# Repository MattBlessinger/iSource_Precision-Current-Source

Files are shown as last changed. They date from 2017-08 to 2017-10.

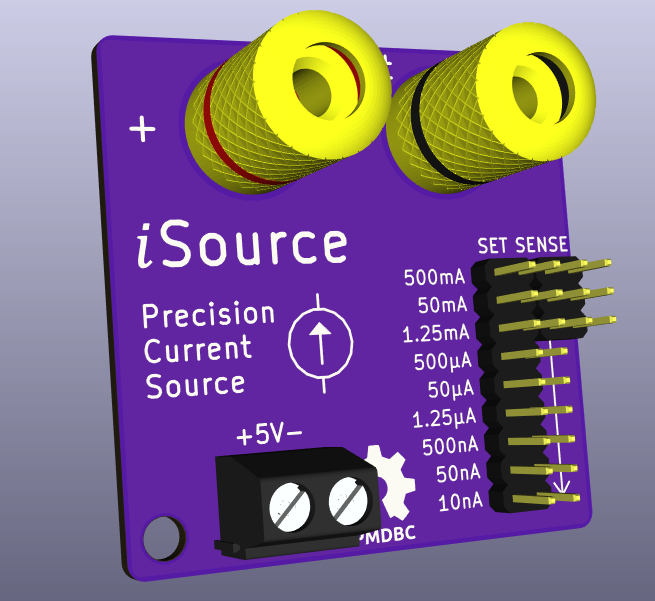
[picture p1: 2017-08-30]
3D top iso.png

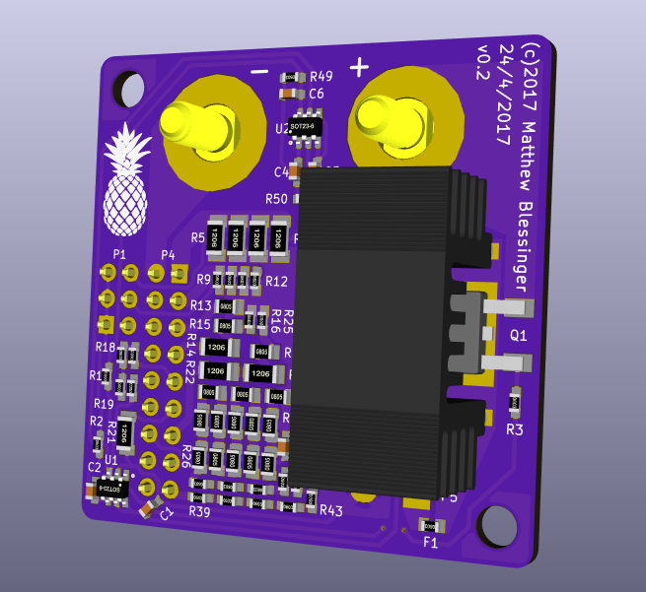
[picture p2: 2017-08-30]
3D bottom iso.png

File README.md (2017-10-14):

# Precision-Current-Source
Low-cost precision current source for calibrating multimeters, ammeters, current shunts, etc.

### Overview
The current source is based on an electronic load in which an op amp sets a known voltage drop across precision resistors. To maintain accuracy, the set-point voltage is constant and sourced by the MAX6070 low-noise, high-precision voltage reference. Different currents are selected by changing the shunt resistors with a pin header jumper. The initial accuracy without tuning (determined by detailed calculations) is <0.1% for 500mA, <0.1% for currents of 50mA to 500nA, <0.2% for 50nA, and <0.5% for 10nA. The measured accuracy was found to be within the expected values except for the nA ranges, likely due to measurement error (see the results spreadsheet file).

### Usage
To use the current source, connect the device under test (DUT) (multimeter, etc.) to the Output +/- 4mm banana connectors on the iSource. (This setup is high-side current sensing.) Put the current set and sense jumpers in the desired position; note that the bottom sense position applies to the set currents of 1.25mA and below. Connect power leads to the screw terminal block and apply power. The current set and sense jumpers can be changed while power is applied without harming the iSource.

### Design
The electronic load design is well-known amongst the electronics community. A commonly referenced design is "EEVBlog 102 – DIY Constant Current Dummy Load for Power Supply and Battery Test." In short, the op amp controls the mosfet's gate voltage to vary the voltage drop across shunt resistors between the mosfet source and ground. The voltage drop is fed to the inverting input of the op amp to provide closed-loop feedback. The set point voltage is routed to the non-inverting input of the op amp. The difference from an electronic load is that the set point voltage does not vary, instead it is constant and supplied by a precision voltage reference. To change the current, the shunt resistors are changed. The DUT is wired between Vdd and the mosfet drain.

The current ranges were chosen based on my initial desire to calibrate my 6000 count multimeter and the EEVBlog uCurrent, hence the 50, 500 and 1250 values. The ranges can be changed by using different resistor combinations. The banana jacks are spaced at the industry standard 0.75". The power input is labeled as 5V but can work down to 4V, e.g. Li-Ion cell. Pin headers and jumpers were used to select the current ranges since low-leakage JFETs can't handle the higher current ranges, and dip switches can't switch the higher either. A parallel load was added to impose a minimum 3mA current through the mosfet to eliminate leakage current issues in the nA ranges. Separate sense pins are used for the 50 and 500mA ranges to account for voltage drop along the tracks due to the higher current. (Voltage drop along the tracks are included in the accuracy calculations for all current ranges.) A DPAK mosfet was used in order to use a heatsink since the mosfet will dissipate a fair amount of heat at 500mA range. It is desired to take the heat away from the PCB in order to not heat the resistors, op amp and voltage reference.

The component choices typically came down to accuracy and cost. The voltage reference gives 0.04% initial accuracy and low thermal drift for $3.35 in one off quantities. The op amp has low input offset voltage (8uV), low input offset current (5pA), and low gain-bandwidth product (80kHz) to prevent the common ringing problem, all for $1.15 in one off quantities. The highest precision resistors were used for a each current range, so cost was minimized by the selection of resistor combinations.

### Accuracy
Several steps were taken to account for the current-induced voltage drop along tracks. As previously mentioned separate sense pins are used for 50 and 500mA so that separate tracks are run to the net-zero middle of the resistor pack. The op amp's ground is run to the net-zero middle of 500mA resistor ground pack since it has the greatest voltage drop. A large ground pour is used to minimuze the resistance between the ground of the op amp and rest of the current ranges' ground return.

Extensive calculations were performed to determine the maximum guaranteed tolerance for an as-built unit. (I did not want to rely on tuning each current range.) The calculations assume worst case scenario for all specifications provided in data sheets, thus the numbers ought to be maximum accuracy values. The parameters included in the accuracy calculations are:
* **Voltage reference**: initial accuracy, thermal drift, thermal hysteresis
* **Resistors**: tolerance, thermal coefficient
* **Op amp**: offset voltage, input bias current, input offset current
* **Track resistance**: resistance from sense pin to first resistor, resistance from last resistor to voltage reference ground, optimized track routing of high-current settings

### Results
I measured the accuracy with a Keysight 34465A 6.5 digit DMM with a 4 month old calibration. The 34465A has a low current range of 1uA with 1pA resolution. I used a single cell lithium ion battery charged to 4.2V to power the iSource. I placed the battery and iSource in a cast aluminum case to minimize EMI. The output was wired to the 34465A with an unshielded twisted pair wires. I used remote logging via PyVISA to remove myself from the measurement area. The 34465A was warmed up for 1 hour, and each current range was allowed to settle for 5 minutes before collecting data, although the currents settled within 10-30 seconds. I took 500 measurements with 10 NPLC at the lowest 34465A current range possible.

The spreadsheet shows the average value, accuracy % based on the measured average, 34465A uncertainty, and standard deviation of the 500 measurements. I suspect the increased inaccuracy of nA ranges is due to my measurement setup as I do not know all the proper techniques nor have the proper setup for them.

### Cost
As of June, 2017, the total build cost was $48 including the OSHPark PCB not listed in the BOM. Lower tolerance resistors may be used to significantly reduce the cost. New accuracy calculations can be performed by changing the resistor tolerance in the spreadsheet.

### License
The project is licensed as open source hardware and Creative Commons Attribution-ShareAlike 3.0 (CC BY-SA 3.0 US)

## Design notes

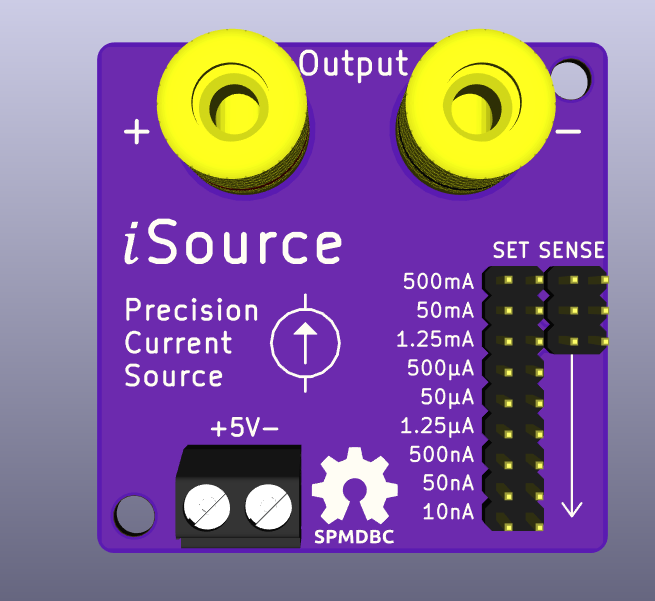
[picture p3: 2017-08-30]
3D top.png

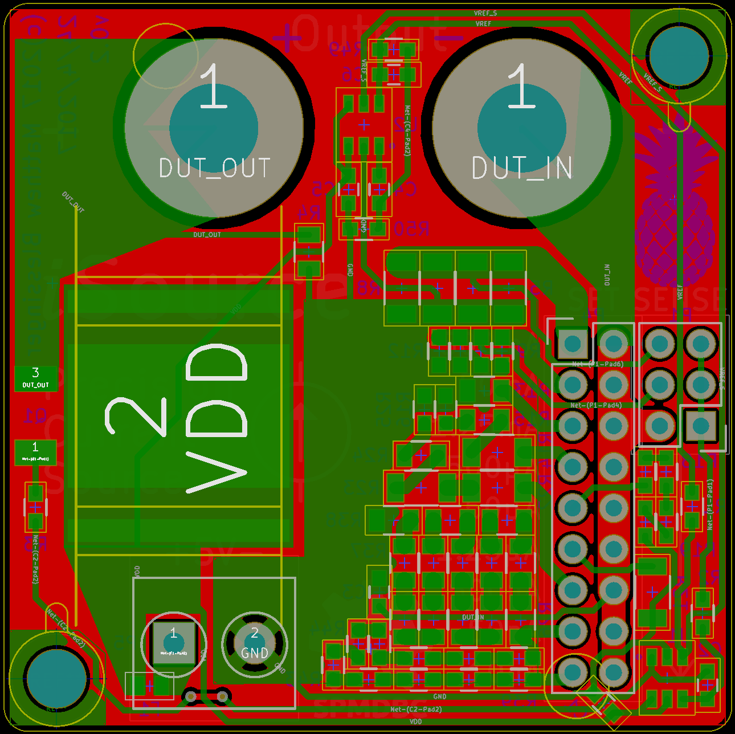
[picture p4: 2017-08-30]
PCB bottom layer.png

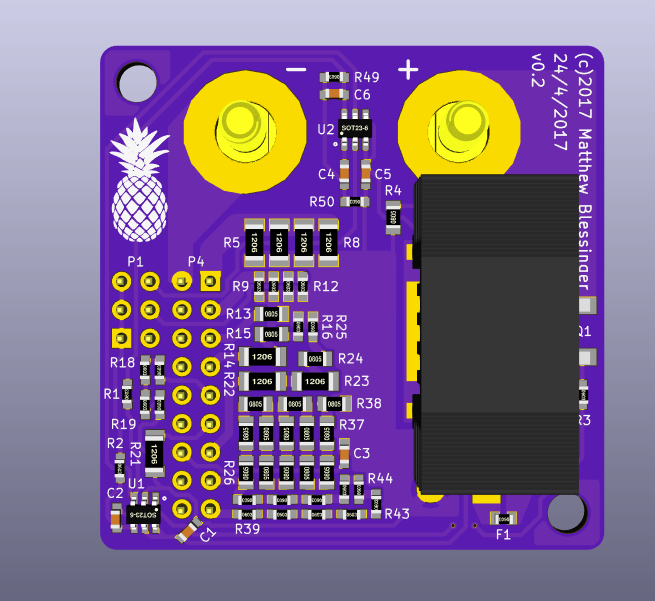
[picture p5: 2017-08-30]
3D bottom.png

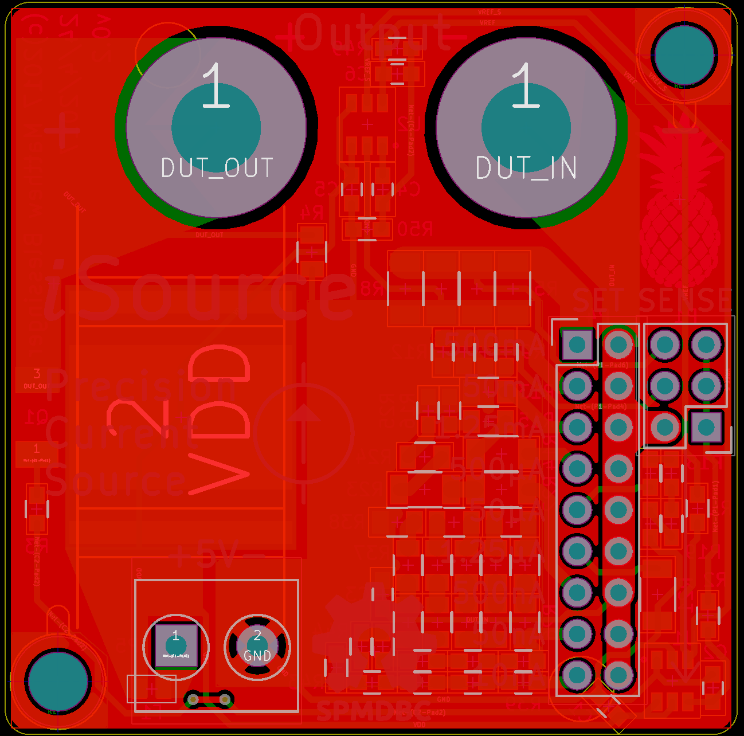
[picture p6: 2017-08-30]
PCB top layer.png

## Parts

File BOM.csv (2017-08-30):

Reference | Value | Footprint | Datasheet | Product ID | Manufacturer | Tolerance
C1 | 0.1uF | MKB:C_0603 |  | GCM188R71H104KA57D | Murata
C5 | 0.1uF | MKB:C_0603 |  | GCM188R71H104KA57D | Murata
C6 | 0.1uF | MKB:C_0603 |  | GCM188R71H104KA57D | Murata
C4 | 0.1uF | MKB:C_0603 |  | GCM188R71H104KA57D | Murata
R50 | 0R | MKB:R_0603 |  | RC0603FR-072KL | Yageo | 1%
R9 | 100R | MKB:R_0603 |  | APC0603T100RZ | Ohmite | 0.01%
R10 | 100R | MKB:R_0603 |  | APC0603T100RZ | Ohmite | 0.01%
R11 | 100R | MKB:R_0603 |  | APC0603T100RZ | Ohmite | 0.01%
R12 | 100R | MKB:R_0603 |  | APC0603T100RZ | Ohmite | 0.01%
R3 | 100R | MKB:R_0603 |  | RC0603FR-07100RL | Yageo
R17 | 10k | MKB:R_0603 |  | APC0603T10K0Z | Ohmite | 0.01%
R18 | 10k | MKB:R_0603 |  | APC0603T10K0Z | Ohmite | 0.01%
R2 | 10k | MKB:R_0603 |  | RC0603FR-0710KL | Yageo
R39 | 10M | MKB:R_0603 |  | CRCW060310M0DHEAP | Vishay Dale | 0.50%
R40 | 10M | MKB:R_0603 |  | CRCW060310M0DHEAP | Vishay Dale | 0.50%
R41 | 10M | MKB:R_0603 |  | CRCW060310M0DHEAP | Vishay Dale | 0.50%
R42 | 10M | MKB:R_0603 |  | CRCW060310M0DHEAP | Vishay Dale | 0.50%
R43 | 10M | MKB:R_0603 |  | CRCW060310M0DHEAP | Vishay Dale | 0.50%
R44 | 10M | MKB:R_0603 |  | CRCW060310M0DHEAP | Vishay Dale | 0.50%
R45 | 10M | MKB:R_0603 |  | CRCW060310M0DHEAP | Vishay Dale | 0.50%
R46 | 10M | MKB:R_0603 |  | CRCW060310M0DHEAP | Vishay Dale | 0.50%
R47 | 10M | MKB:R_0603 |  | CRCW060310M0DHEAP | Vishay Dale | 0.50%
R48 | 10M | MKB:R_0603 |  | CRCW060310M0DHEAP | Vishay Dale | 0.50%
C2 | 10nF | MKB:C_0603 |  | GRM188R71H103JA01D | Murata
R20 | 10R | MKB:R_0603 |  | RC0603FR-0710RL | Yageo | 1%
R5 | 10R | MKB:R_1206 |  | RNCF1206AKT10R0 | Stackpole Electronics | 0.05%
R6 | 10R | MKB:R_1206 |  | RNCF1206AKT10R0 | Stackpole Electronics | 0.05%
R7 | 10R | MKB:R_1206 |  | RNCF1206AKT10R0 | Stackpole Electronics | 0.05%
R8 | 10R | MKB:R_1206 |  | RNCF1206AKT10R0 | Stackpole Electronics | 0.05%
R13 | 1k | MKB:R_0805 |  | APC0805T1K00Z | Ohmite | 0.01%
R38 | 1M | MKB:R_0805 |  | CPF0805B1M0E1 | TE Connectivity | 0.10%
R21 | 1M | MKB:R_1206 |  | RG3216N-1004-W-T1 | Susumu | 0.05%
R22 | 1M | MKB:R_1206 |  | RG3216N-1004-W-T1 | Susumu | 0.05%
R23 | 1M | MKB:R_1206 |  | RG3216N-1004-W-T1 | Susumu | 0.05%
R16 | 1R | MKB:R_0603 |  | RC0603FR-071RL | Yageo | 1%
C3 | 1uF | MKB:C_0603 |  | GCM188R71H104KA57D | Murata
R1 | 270R | MKB:R_0603 |  | RC0603FR-07270RL | Yageo
R14 | 2k | MKB:R_1206 |  | APC1206T2K00Z | Ohmite | 0.01%
R49 | 2k | MKB:R_0603 |  | RC0603FR-072KL | Yageo | 1%
R26 | 2M | MKB:R_0805 |  | CPF0805B2M0E1 | TE Connectivity | 0.10%
R27 | 2M | MKB:R_0805 |  | CPF0805B2M0E1 | TE Connectivity | 0.10%
R28 | 2M | MKB:R_0805 |  | CPF0805B2M0E1 | TE Connectivity | 0.10%
R29 | 2M | MKB:R_0805 |  | CPF0805B2M0E1 | TE Connectivity | 0.10%
R30 | 2M | MKB:R_0805 |  | CPF0805B2M0E1 | TE Connectivity | 0.10%
R31 | 2M | MKB:R_0805 |  | CPF0805B2M0E1 | TE Connectivity | 0.10%
R32 | 2M | MKB:R_0805 |  | CPF0805B2M0E1 | TE Connectivity | 0.10%
R33 | 2M | MKB:R_0805 |  | CPF0805B2M0E1 | TE Connectivity | 0.10%
R34 | 2M | MKB:R_0805 |  | CPF0805B2M0E1 | TE Connectivity | 0.10%
R35 | 2M | MKB:R_0805 |  | CPF0805B2M0E1 | TE Connectivity | 0.10%
R36 | 2M | MKB:R_0805 |  | CPF0805B2M0E1 | TE Connectivity | 0.10%
R37 | 2M | MKB:R_0805 |  | CPF0805B2M0E1 | TE Connectivity | 0.10%
R25 | 30k | MKB:R_0603 |  | RG1608N-303-W-T1 | Susumu | 0.05%
R24 | 470k | MKB:R_0805 |  | RG2012N-474-W-T1 | Susumu | 0.05%
R4 | 470R | MKB:R_0805 |  | RC0805FR-07470RL | Yageo
R15 | 499R | MKB:R_0805 |  | APC0805T499RZ | Ohmite | 0.01%
R19 | 4k99 | MKB:R_0603 |  | APC0603T4K99Z | Ohmite | 0.01%
F1 | 750mA | MKB:FUSE_0603 |  | C2Q 750 | Bel Fuse
P2 | CONN_01X01 | MKB:Binding_post_4mm |  | _ | _
P3 | CONN_01X01 | MKB:Binding_post_4mm |  | _ | _
P5 | CONN_01X02 | MKB:TerminalBlock_Pheonix_MKDS1.5-2pol_1985849 |  | 1985849 | Phoenix Contact
P1 | CONN_02X03 | Pin_Headers:Pin_Header_Straight_2x03
P4 | CONN_02X09 | Pin_Headers:Pin_Header_Straight_2x09
U2 | MAX6070 | MKB:SOT-23-6 |  | MAX6070AAUT12+T | Maxim Integrated
U1 | MCP6V11T-E/OT | MKB:SOT-23-6 |  | MCP6V11T-E/OT | Microchip
Q1 | Q_NMOS_GDS | MKB:TO-252_wHeatsink |  | BUK92150-55A_118 | Nexperia
 | case |  |  | 1551RBK | Hammond Manufacturing
 | heat sink |  |  | 219-263A-TR | Wakefield-Vette

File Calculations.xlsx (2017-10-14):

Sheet: Summary
I_designed [A] | U_designed [%] | I_measured [A] | U_measured [%]
0.5 | 0.1364
0.05 | 0.0791 | 0.04999793058 | 0.0041
0.00125 | 0.0789 | 0.0012498142 | 0.0149
0.0005 | 0.0758 | 0.0004999797453 | 0.0041
5e-05 | 0.0750 | 4.999951055e-05 | 0.0010
1.25e-06 | 0.1146 | 1.250664623e-06 | 0.0532
5e-07 | 0.1146 | 5.0069806e-07 | 0.1396
5e-08 | 0.1647 | 5.063922111e-08 | 1.2784
1e-08 | 0.4866 | 1.064807622e-08 | 6.4808

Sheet: Measurements
I_designed [A] | I_measured [A] | Error [%] | Standard dev [A] | Uncertainty [A] | Uncertainty [%]
0.5
0.05 | 0.04999793058 | -0.0041 | 1.492796574e-07 | 2.999896529e-05 | 0.0600
0.00125 | 0.0012498142 | -0.0149 | 3.650786754e-08 | 2.6249071e-06 | 0.2100
0.0005 | 0.0004999797453 | -0.0041 | 1.001276153e-09 | 2.999898727e-07 | 0.0600
5e-05 | 4.999951055e-05 | -0.0010 | 1.323088922e-10 | 2.599975528e-08 | 0.0520
1.25e-06 | 1.250664623e-06 | 0.0532 | 9.79271387e-11 | 8.253323114e-10 | 0.0660
5e-07 | 5.0069806e-07 | 0.1396 | 9.602042023e-11 | 3.0034903e-10 | 0.0600
5e-08 | 5.063922111e-08 | 1.2784 | 9.551141511e-11 | 7.531961055e-11 | 0.1487
1e-08 | 1.064807622e-08 | 6.4808 | 9.215407967e-11 | 5.532403811e-11 | 0.5196
All measurements were made with a Keysight 34465A with a calibration date of less than 1 year.
The 34465A was warmed up for at least 1 hour before measurements and then an autocalibration was performed.
All measurements were taken with 10 NPLC, auto zero, and the lowest current range possible.
The DUT reading was allowed to stabilize for 2 minutes (typically took less than 30 seconds) before data recording.
500 data points were taken for each current setting (~3 minutes).
The measurement uncertainty was calculated using the 1-year values specified in the 34465A manual.

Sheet: Designed tolerance
 |  |  |  |  |  | Resistors |  |  | Voltage reference |  |  |  |  |  | Trace resistance |  | Op amp
V_ref [V] | R [Ω] | I [A] | U [%] |  | T [C] | Total tol [%] | R_tol [%] | T_coeff [ppm/C] | Total tol [%] | Base tol [%] | T drift [%] | Line reg [μV/V] | Load reg [μV/mA] | Long-term [%] | Sense offset [%] | Gnd offset [%] | Total tol [%] | Vos [%] | T drift [%] | Ib [%] | Ios [%]
1.25 | 2.5 | 0.5 | 0.136 | 0.5006820275 | 50 | 0.056 | 0.050 | 10 | 0.066 | 0.04 | 0.0150 | 0.0500 | 0.0075 | 0.0035 | 0.0318 | 0.02770 | 0.00065 | 0.00064 | 0.0001 | 1.36e-05 | 6.4e-05
 | 25 | 0.05 | 0.079 | 0.05003952587 | 35 | 0.011 | 0.010 | 5 | 0.065 | 0.04 | 0.0060 | 0.0500 | 0.0075 | 0.0035 | 0.0038 | 0.00789 | 0.00064 | 0.00064 | 4e-05 | 1.36e-05 | 6.4e-05
 | 1000 | 0.00125 | 0.079 | 0.001250986833 | 25 | 0.010 | 0.010 | 5 | 0.065 | 0.04 | 0.0000 | 0.0500 | 0.0075 | 0.0035 | 0.0103 | 0.00059468 | 0.00064 | 0.00064 | 0.0000 | 1.36e-05 | 6.4e-05
 | 2500 | 0.0005 | 0.076 | 0.0005003788138 | 25 | 0.010 | 0.010 | 5.1 | 0.065 | 0.04 | 0.0000 | 0.0500 | 0.0075 | 0.0035 | 0.0041 | 0.00048248 | 0.00064 | 0.00064 | 0.0000 | 1.36e-05 | 6.4e-05
 | 25000 | 5e-05 | 0.075 | 5.003749721e-05 | 25 | 0.010 | 0.010 | 5.1 | 0.065 | 0.04 | 0.0000 | 0.0500 | 0.0075 | 0.0035 | 0.0004304 | 0.00055088 | 0.00064 | 0.00064 | 0.0000 | 1.36e-05 | 6.4e-05
 | 1000000 | 1.25e-06 | 0.115 | 1.25143283e-06 | 25 | 0.050 | 0.050 | 10 | 0.065 | 0.04 | 0.0000 | 0.0500 | 0.0075 | 0.0035 | 1.089e-05 | 0.00044078 | 0.00064 | 0.00064 | 0.0000 | 1.36e-05 | 6.4e-05
 | 2500000 | 5e-07 | 0.115 | 5.005731305e-07 | 25 | 0.050 | 0.050 | 10 | 0.065 | 0.04 | 0.0000 | 0.0500 | 0.0075 | 0.0035 | 4.296e-06 | 0.0004077548 | 0.00064 | 0.00064 | 0.0000 | 1.36e-05 | 6.4e-05
 | 25000000 | 5e-08 | 0.165 | 5.008236638e-08 | 25 | 0.100 | 0.100 | 25 | 0.065 | 0.04 | 0.0000 | 0.0500 | 0.0075 | 0.0035 | 4.196e-07 | 0.00042224 | 0.00064 | 0.00064 | 0.0000 | 1.36e-05 | 6.4e-05
 | 125000000 | 1e-08 | 0.487 | 1.004866111e-08 | 25 | 0.420 | 0.420 | 50 | 0.065 | 0.04 | 0.0000 | 0.0500 | 0.0075 | 0.0035 | 8.392e-08 | 0.00042224 | 0.00064 | 0.00064 | 0.0000 | 1.36e-05 | 6.4e-05

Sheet: Resistor configuration
V_ref [V] | R [Ω] | I [A] | P [W] | Resistor config | R_tol [%] | P_R [W] | T_coeff [ppm/C] | Package | Part #
1.25 | 2.5 | 0.5 | 0.625000000 | 4//10R .05% | 0.050 | 1 | 10 | 1206 | RNCF1206AKT10R0
 | 25 | 0.05 | 0.062500000 | 4//100R .01% | 0.010 | 0.25 | 5 | 0603 | APC0603T100RZ
 | 1000 | 0.00125 | 0.001562500 | 1k .01% | 0.010 | 0.1 | 5 | 0805 | APC0805T1K00Z
 | 2500 | 0.0005 | 0.000625000 | 2k, 499R .01%, 1R 1% | 0.010 | 0.120 | 5.1 | 1206 0805 0603 | APC1206T2K00Z APC0805T499RZ RC0603FR-071RL
 | 25000 | 5e-05 | 0.000062500 | 2x10k, 4.99k .01%, 10R 1% | 0.010 | 0.062479 | 5.1 | 0603 0603 0603 | APC0603T10K0Z APC0603T4K99Z RC0603FR-0710RL
 | 1000000 | 1.25e-06 | 0.000001563 | 1M .05% | 0.050 | 0.25 | 10 | 1206 | RG3216N-1004-W-T1
 | 2500000 | 5e-07 | 0.000000625 | 2x1M, 470k, 30k .05% | 0.050 | 0.225 | 10 | 1206 0805 0603 | RG3216N-1004-W-T1 RG2012N-474-W-T1 RG1608N-303-W-T1
 | 25000000 | 5e-08 | 0.000000062 | 12x2M, 1M .1% | 0.100 | 1.3 | 25 | 0805 | CPF0805B2M0E1 CPF0805B1M0E1
 | 125000000 | 1e-08 | 0.000000012 | 10x10M .5%, 12x2M, 1M .1% | 0.420 | 1.08 | 50 | 0603 | CRCW060310M0DHEAP

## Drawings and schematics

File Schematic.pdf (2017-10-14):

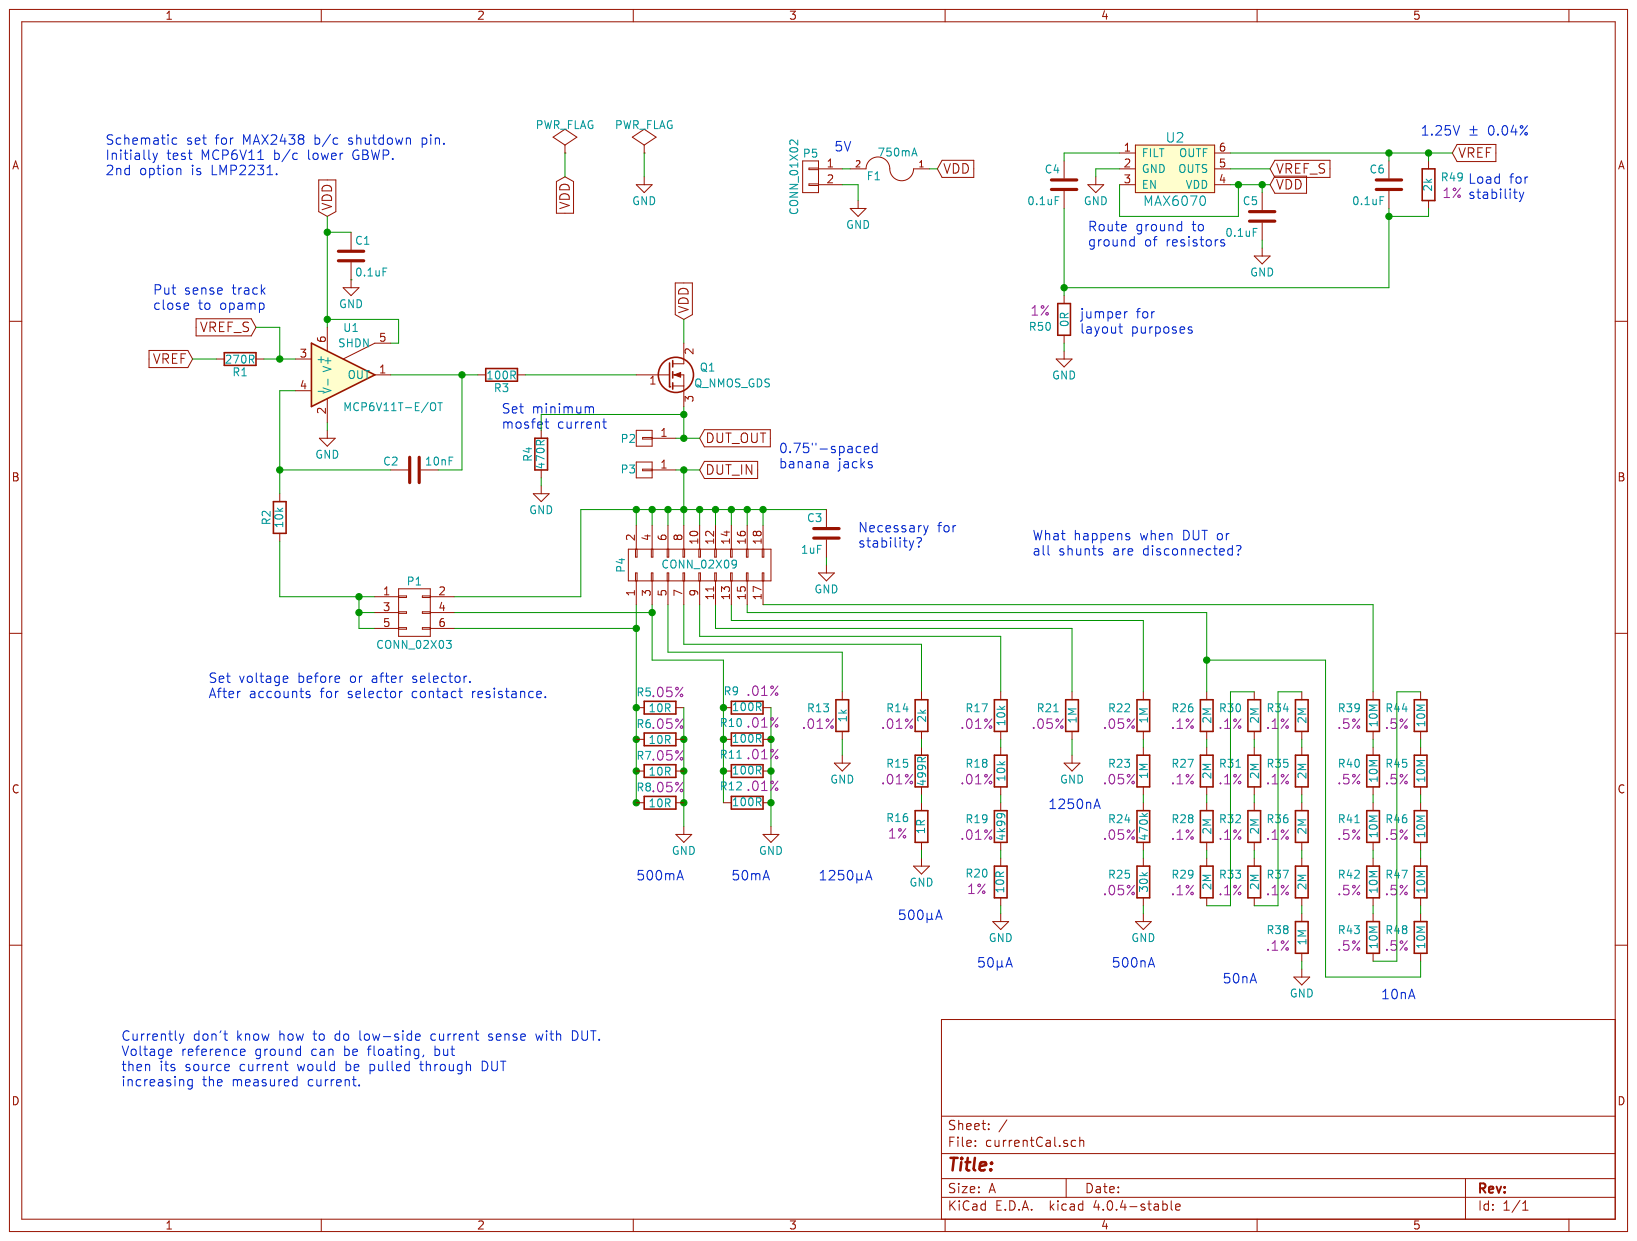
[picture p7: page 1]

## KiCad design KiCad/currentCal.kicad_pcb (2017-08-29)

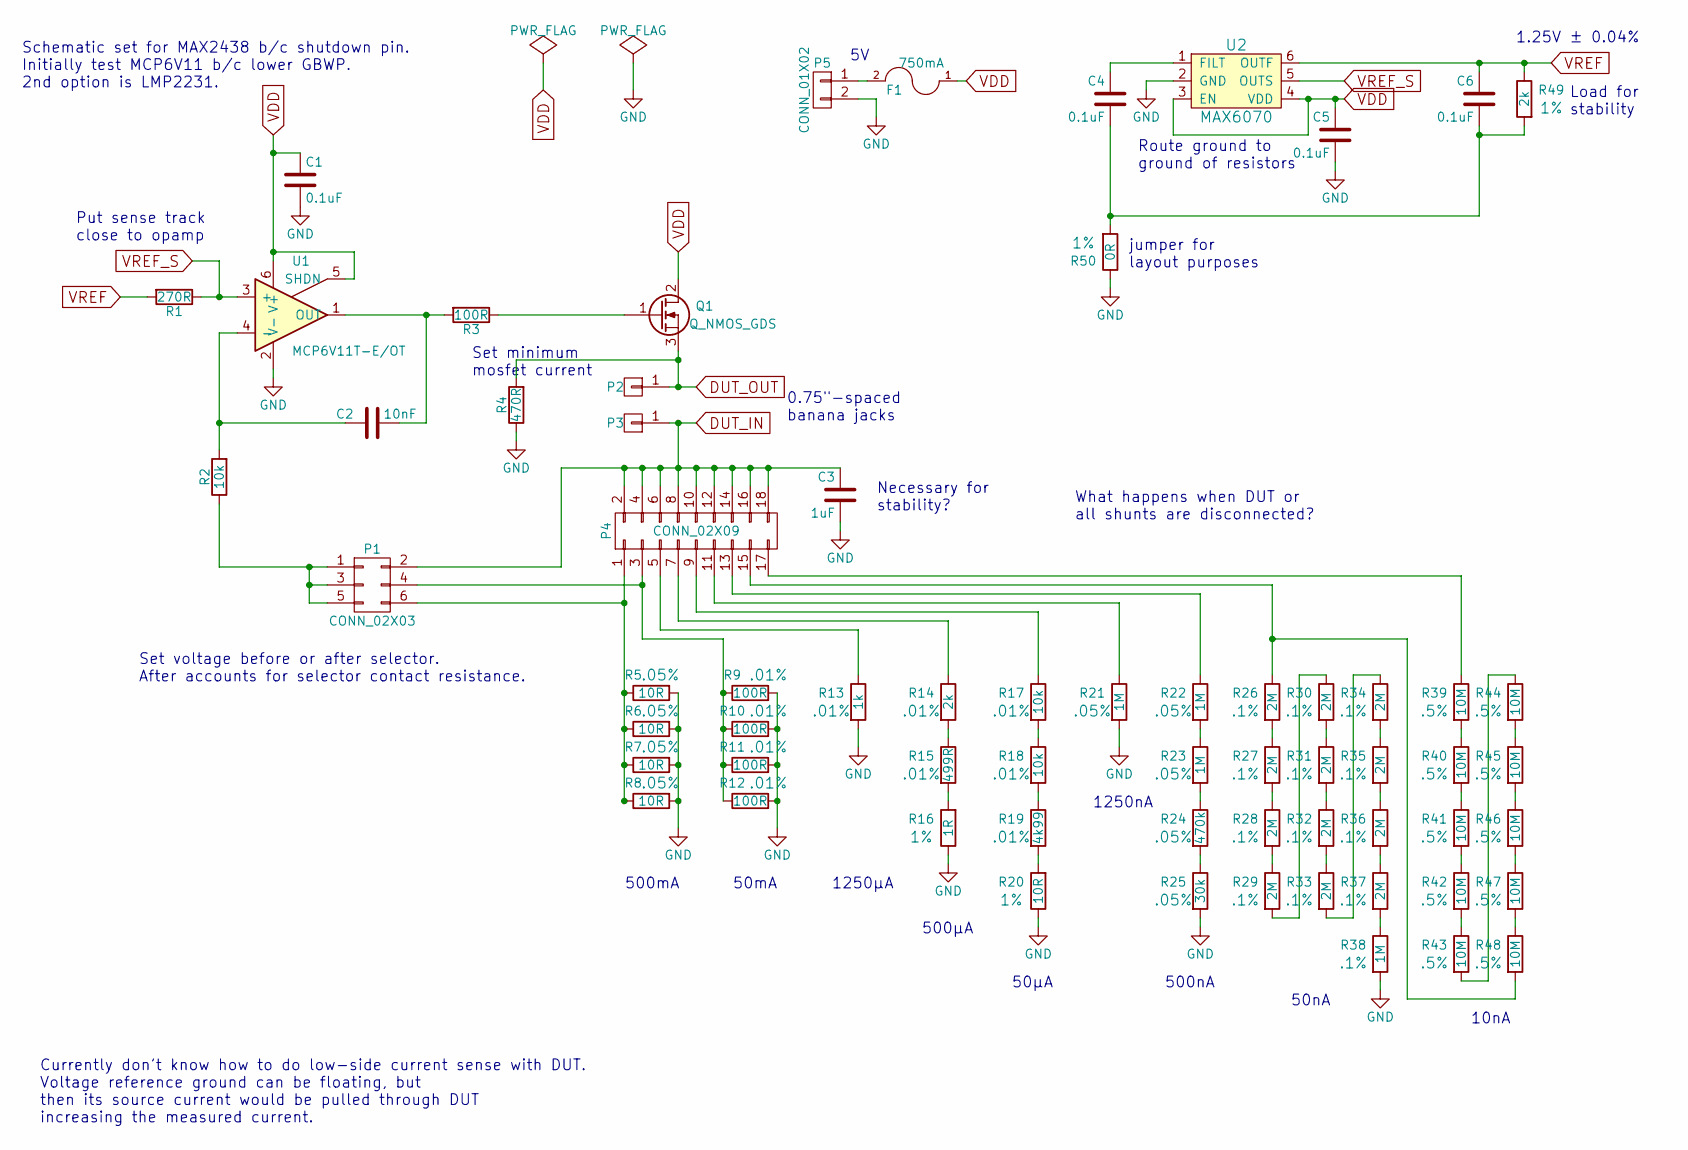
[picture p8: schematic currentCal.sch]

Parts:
C1, C4, C5, C6: 0.1uF; C_0603
C2: 10nF; C_0603
C3: 1uF; C_0603
F1: 750mA; FUSE_0603
P1: CONN_02X03; Pin_Header_Straight_2x03
P2, P3: CONN_01X01; Binding_post_4mm
P4: CONN_02X09; Pin_Header_Straight_2x09
P5: CONN_01X02; TerminalBlock_Pheonix_MKDS1.5-2pol_1985849
Q1: Q_NMOS_GDS; TO-252_wHeatsink
R1: 270R; R_0603
R2: 10k; R_0603
R3: 100R; R_0603
R4: 470R; R_0805
R5, R6, R7, R8: 10R; R_1206; Tolerance .05%
R9, R10, R11, R12: 100R; R_0603; Tolerance .01%
R13: 1k; R_0805; Tolerance .01%
R14: 2k; R_1206; Tolerance .01%
R15: 499R; R_0805; Tolerance .01%
R16: 1R; R_0603; Tolerance 1%
R17, R18: 10k; R_0603; Tolerance .01%
R19: 4k99; R_0603; Tolerance .01%
R20: 10R; R_0603; Tolerance 1%
R21, R22, R23: 1M; R_1206; Tolerance .05%
R24: 470k; R_0805; Tolerance .05%
R25: 30k; R_0603; Tolerance .05%
R26, R27, R28, R29, R30, R31, R32, R33, R34, R35, R36, R37: 2M; R_0805; Tolerance .1%
R38: 1M; R_0805; Tolerance .1%
R39, R40, R41, R42, R43, R44, R45, R46, R47, R48: 10M; R_0603; Tolerance .5%
R49: 2k; R_0603; Tolerance 1%
R50: 0R; R_0603; Tolerance 1%
U1: MCP6V11T-E/OT; SOT-23-6
U2: MAX6070; SOT-23-6

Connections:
DUT_IN: C3.1, P1.2, P3.1, P4.2, P4.4, P4.6, P4.8, P4.10, P4.12, P4.14, P4.16, P4.18
DUT_OUT: P2.1, Q1.3 (S), R4.2
GND: C1.2, C3.2, C5.2, P5.2, R4.1, R5.2, R6.2, R7.2, R8.2, R9.2, R10.2, R11.2, R12.2, R13.2, R16.1, R20.1, R21.2, R25.2, R38.2, R50.1, U1.2 (V-), U2.2 (GND)
unnamed: C2.1, R2.2, U1.4 (-)
unnamed: C2.2, R3.2, U1.1 (OUT)
unnamed: C4.1, U2.1 (FILT)
unnamed: C4.2, C6.2, R49.2, R50.2
unnamed: F1.2, P5.1
unnamed: P1.1, P1.3, P1.5, R2.1
unnamed: P1.4, P4.3, R9.1, R10.1, R11.1, R12.1
unnamed: P1.6, P4.1, R5.1, R6.1, R7.1, R8.1
unnamed: P4.5, R13.1
unnamed: P4.7, R14.1
unnamed: P4.9, R17.1
unnamed: P4.11, R21.1
unnamed: P4.13, R22.1
unnamed: P4.15, R26.1, R48.2
unnamed: P4.17, R39.1
unnamed: Q1.1 (G), R3.1
unnamed: R14.2, R15.1
unnamed: R15.2, R16.2
unnamed: R17.2, R18.1
unnamed: R18.2, R19.1
unnamed: R19.2, R20.2
unnamed: R22.2, R23.1
unnamed: R23.2, R24.1
unnamed: R24.2, R25.1
unnamed: R26.2, R27.1
unnamed: R27.2, R28.1
unnamed: R28.2, R29.1
unnamed: R29.2, R30.1
unnamed: R30.2, R31.1
unnamed: R31.2, R32.1
unnamed: R32.2, R33.1
unnamed: R33.2, R34.1
unnamed: R34.2, R35.1
unnamed: R35.2, R36.1
unnamed: R36.2, R37.1
unnamed: R37.2, R38.1
unnamed: R39.2, R40.1
unnamed: R40.2, R41.1
unnamed: R41.2, R42.1
unnamed: R42.2, R43.1
unnamed: R43.2, R44.1
unnamed: R44.2, R45.1
unnamed: R45.2, R46.1
unnamed: R46.2, R47.1
unnamed: R47.2, R48.1
VDD: C1.1, C5.1, F1.1, Q1.2 (D), U1.5 (SHDN), U1.6 (V+), U2.3 (EN), U2.4 (VDD)
VREF: C6.1, R1.2, R49.1, U2.6 (OUTF)
VREF_S: R1.1, U1.3 (+), U2.5 (OUTS)

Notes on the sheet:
Currently don't know how to do low-side current sense with DUT. Voltage reference ground can be floating, but then its source current would be pulled through DUT increasing the measured current.
Set voltage before or after selector. After accounts for selector contact resistance.
Put sense track close to opamp
Load for stability
1.25V ± 0.04%
Route ground to ground of resistors
0.75"-spaced banana jacks
What happens when DUT or all shunts are disconnected?
Set minimum mosfet current
Schematic set for MAX2438 b/c shutdown pin. Initially test MCP6V11 b/c lower GBWP. 2nd option is LMP2231.
Necessary for stability?
500mA
50mA
1250µA
500µA
50µA
1250nA
500nA
50nA
10nA
jumper for layout purposes

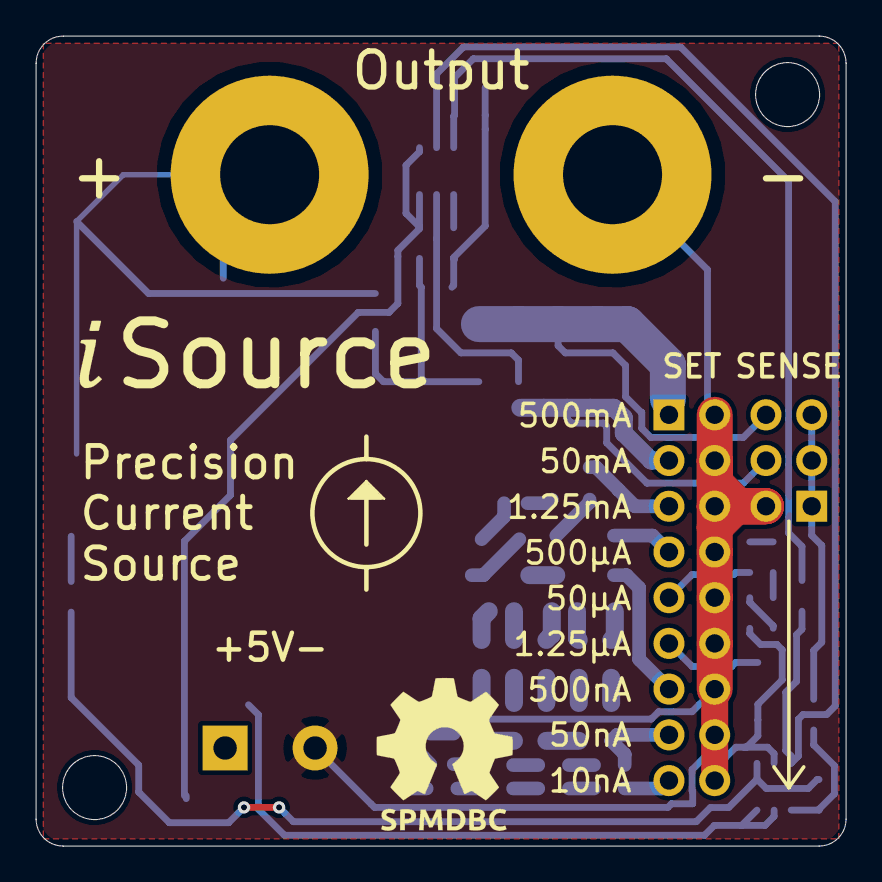
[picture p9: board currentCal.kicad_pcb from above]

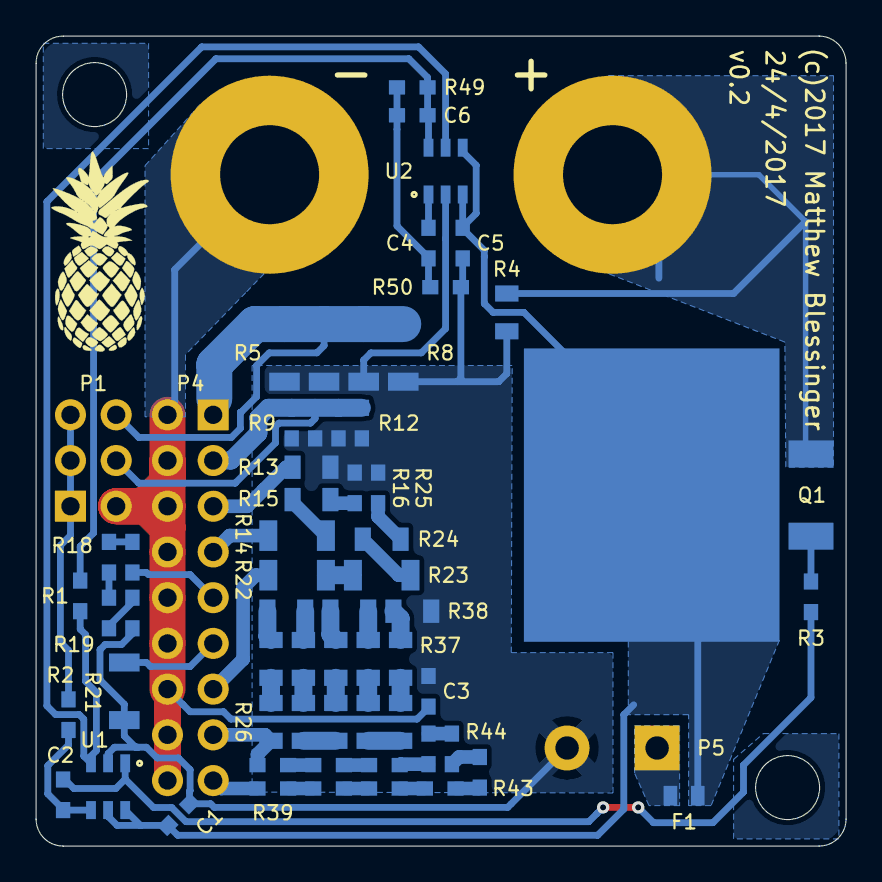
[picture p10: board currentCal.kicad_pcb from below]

Board: 2 copper layers, 45.0 x 45.0 mm, 65 parts (60 on the bottom side), 51 nets.

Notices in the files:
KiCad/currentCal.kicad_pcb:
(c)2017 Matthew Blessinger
